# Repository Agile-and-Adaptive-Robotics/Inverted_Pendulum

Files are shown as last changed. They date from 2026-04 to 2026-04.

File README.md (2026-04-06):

# Inverted Pendulum

This repository contains the files related to the development, construction, and testing of the pneumatically-actuated Inverted Pendulum experimental rig, by members of the Agile & Adaptive Robotics Laboratory at Portland State University. The Inverted Pendulum was developed in tandem with the [Balance Platform](https://github.com/Agile-and-Adaptive-Robotics/Balance_Platform). The pair represents an experimental testbed for exploring perturbed bipedal stance, and was inspired by Peterka, 2002.

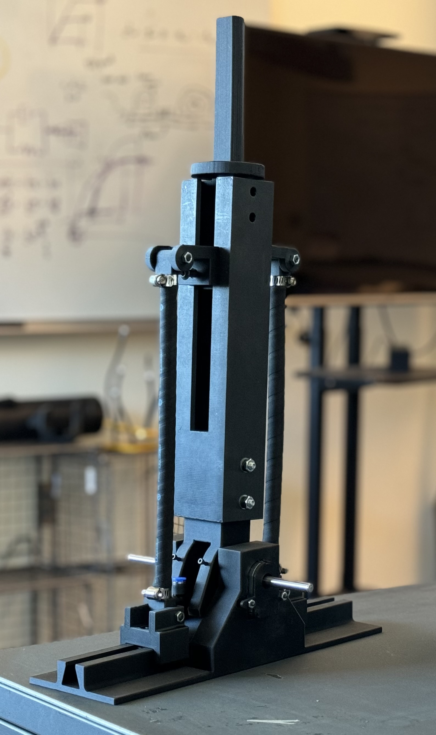
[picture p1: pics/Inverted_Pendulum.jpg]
Platform


Note that this repo is for the pitured version of the Inverted Pendulum. The previous repo was archived and can be accessed [here] (https://github.com/Agile-and-Adaptive-Robotics/Inverted_Pendulum-archive). 

## Contents

- [Software](/code)
  - [README](/code/README.md)
- [datasheets](/datasheets)
  - [README](/datasheets/README.md)
- [pics](/pics)
- [SolidWorks](/SolidWorks)

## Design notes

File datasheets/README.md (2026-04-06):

# Datasheets

This folder is intended to house data sheets for the hardware mounted to the Inverted Pendulum. Any related software should be copied to the proper folder and linked in this README file.

## Hardware 
*link to source, even if a hard copy is present*:

- [Festo_fluidic_muscle_DMSP](https://www.festo.com/us/en/p/fluidic-muscle-id_DMSP/)

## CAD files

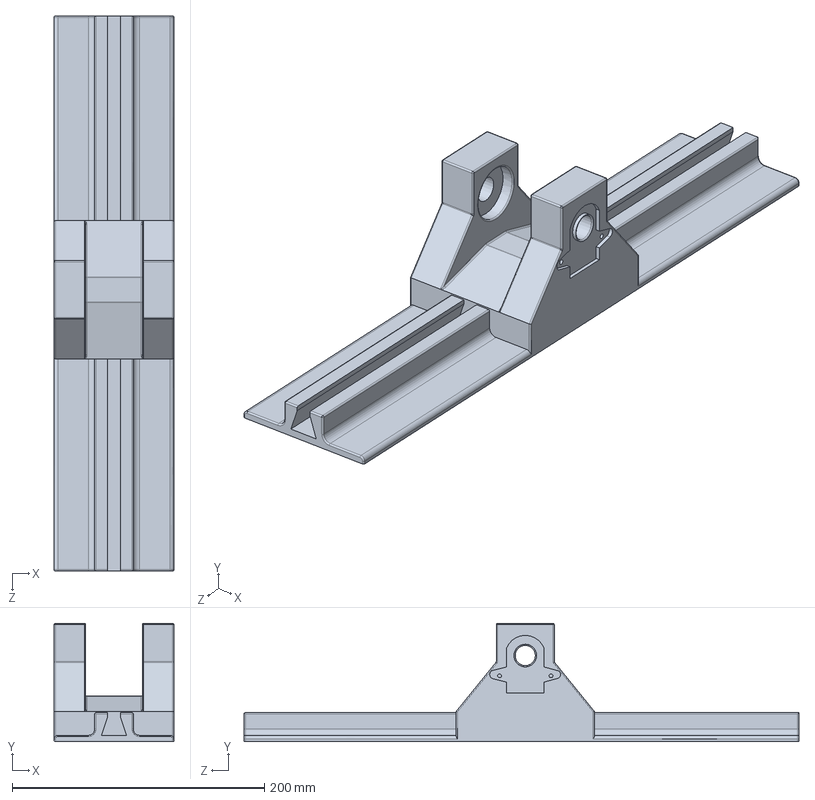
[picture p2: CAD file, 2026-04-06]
SolidWorks/IP_01_00_0000_Mechanical/AARL_IP_BottomPiece_001.SLDPRT
95.0 x 93.8 x 440.0 mm

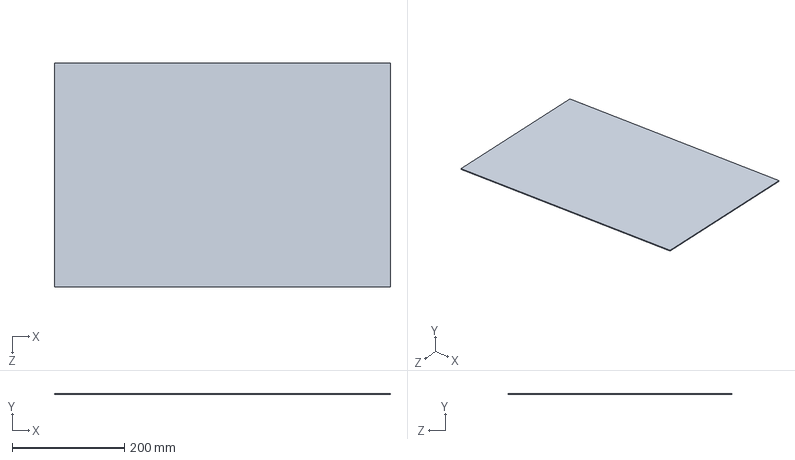
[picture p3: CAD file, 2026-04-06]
SolidWorks/IP_01_00_0000_Mechanical/AARL_IP_BasePlate_001.SLDPRT
600.0 x 2.00 x 400.0 mm

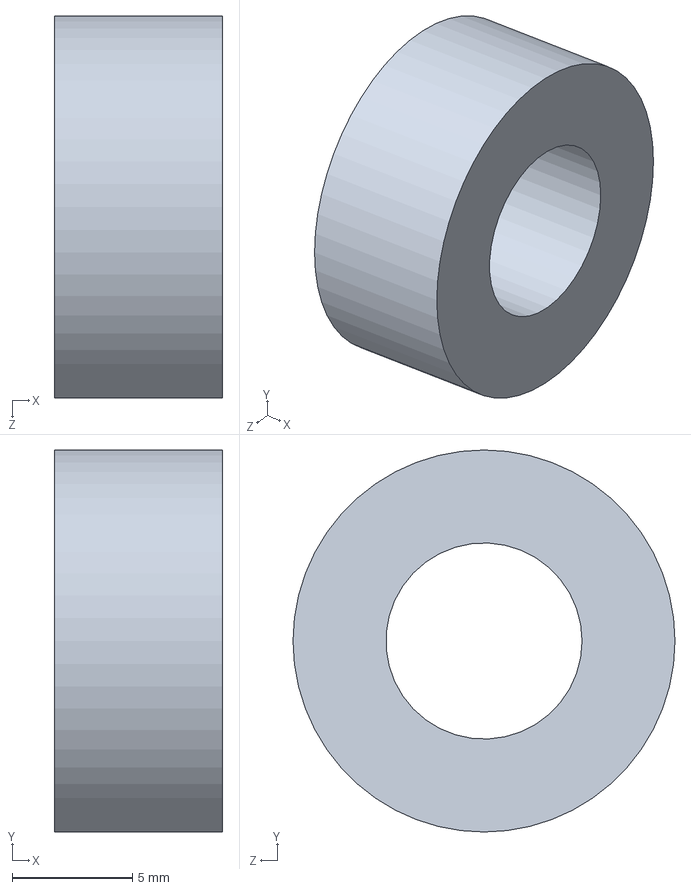
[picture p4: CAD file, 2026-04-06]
SolidWorks/IP_01_00_0000_Mechanical/AARL_IP_Joint_Rod_Insert_001.SLDPRT
7.00 x 15.9 x 15.9 mm

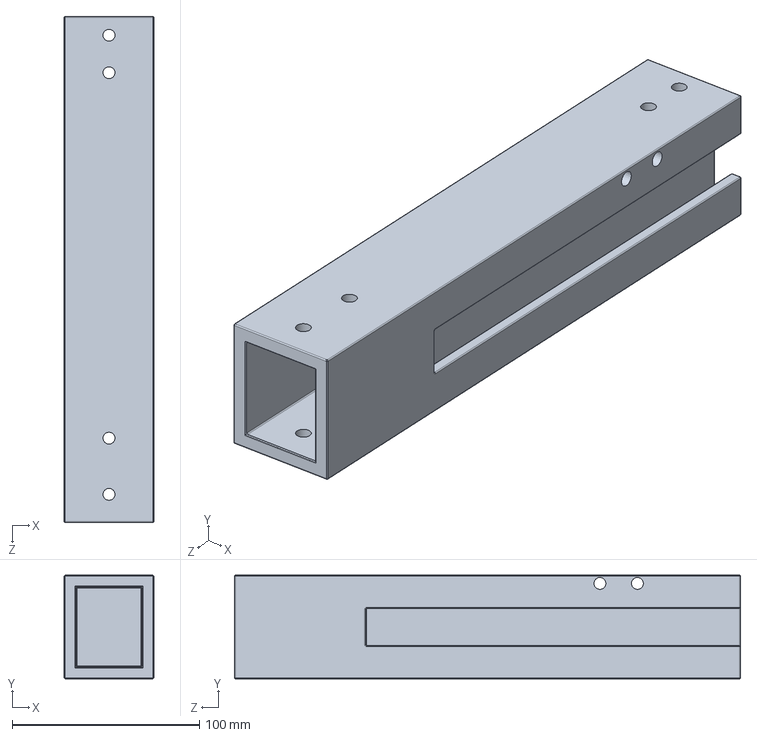
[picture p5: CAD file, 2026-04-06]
SolidWorks/IP_01_00_0000_Mechanical/AARL_IP_CenterPiece_001.SLDPRT
47.8 x 55.3 x 270.0 mm

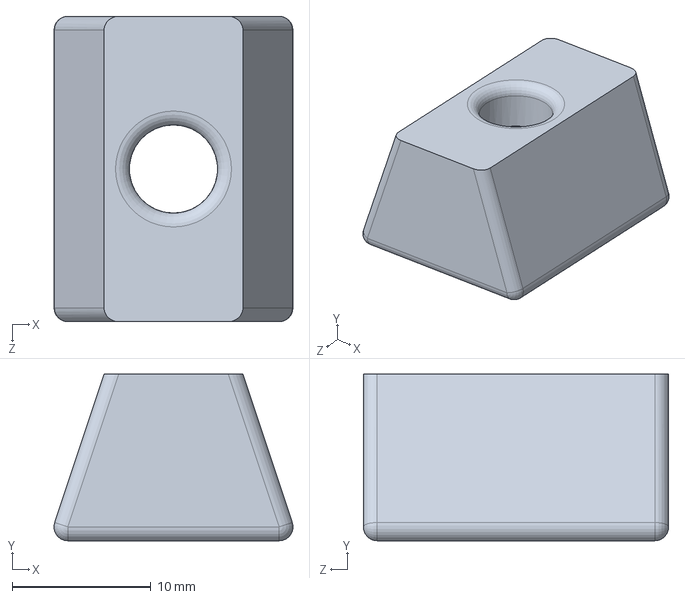
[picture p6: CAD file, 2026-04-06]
SolidWorks/IP_01_00_0000_Mechanical/AARL_IP_BottomSlider_BottomPiece_001.SLDPRT
17.2 x 12.0 x 22.0 mm

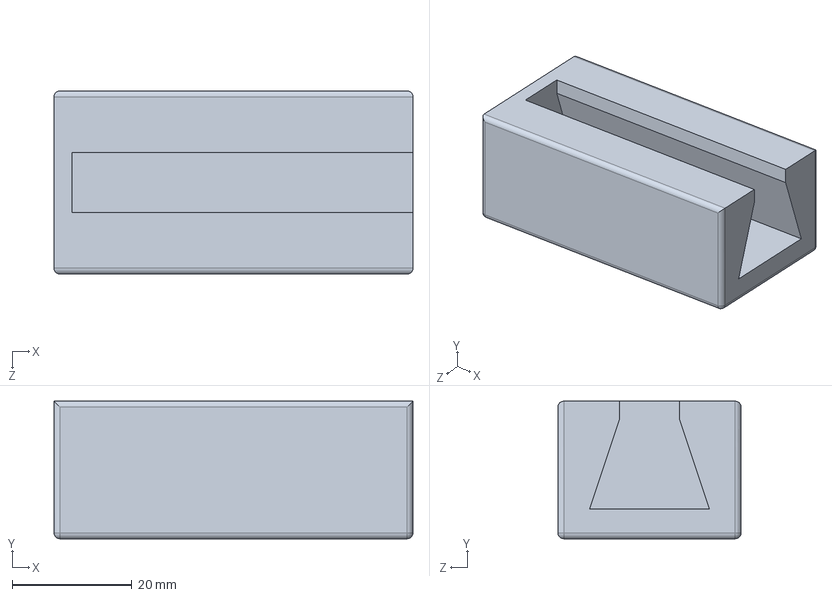
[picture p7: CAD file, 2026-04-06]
SolidWorks/IP_01_00_0000_Mechanical/AARL_IP_BottomPiece_Test_001.SLDPRT
60.0 x 23.0 x 30.7 mm

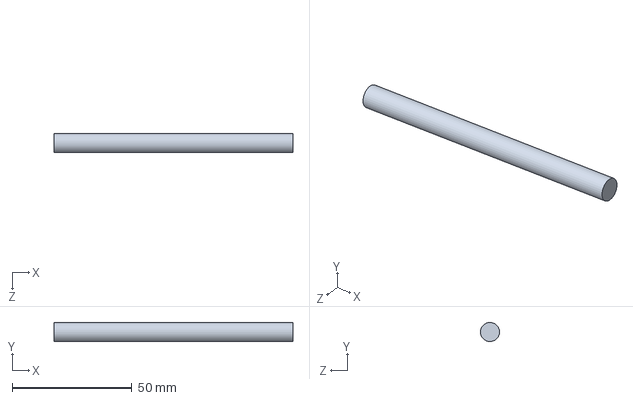
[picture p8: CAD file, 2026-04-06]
SolidWorks/IP_01_00_0000_Mechanical/AARL_IP_Joint_Rod_001.SLDPRT
100.0 x 7.99 x 8.00 mm

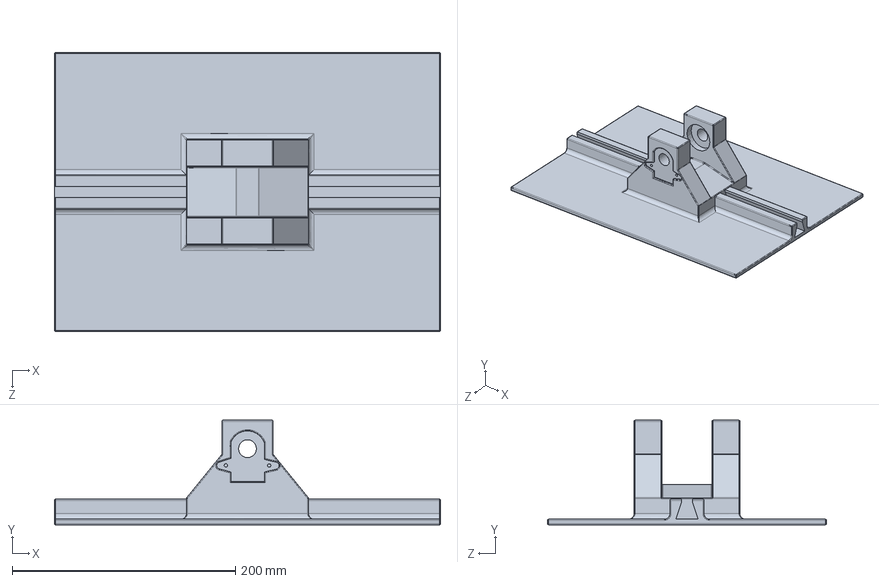
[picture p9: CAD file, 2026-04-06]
SolidWorks/IP_01_00_0000_Mechanical/AARL_IP_BottomPiece_002.SLDPRT
346.0 x 93.8 x 250.0 mm

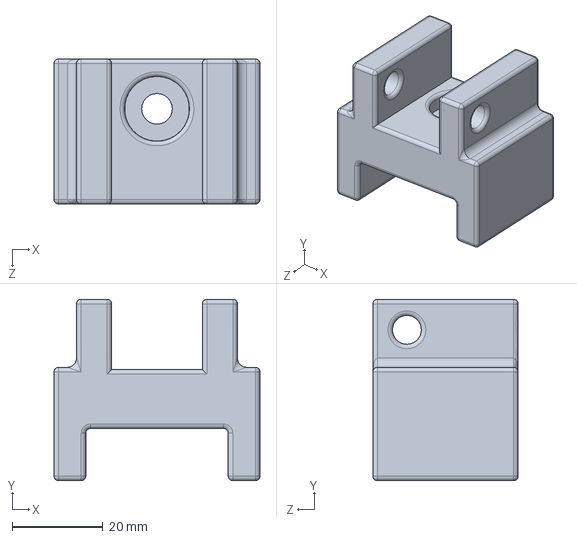
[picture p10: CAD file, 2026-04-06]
SolidWorks/IP_01_00_0000_Mechanical/AARL_IP_BottomSlider_TopPiece_001.SLDPRT
45.4 x 40.0 x 32.0 mm

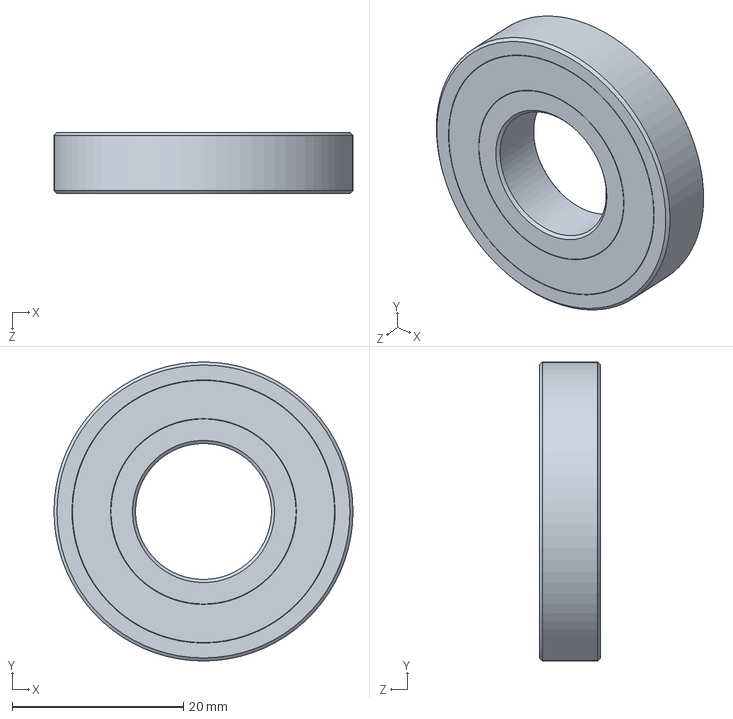
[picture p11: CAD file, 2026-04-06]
SolidWorks/IP_01_00_0000_Mechanical/AARL_IP_Joint_2342K167_PermanentlyLubricatedBallBearing_001.SLDPRT
34.9 x 34.9 x 7.14 mm

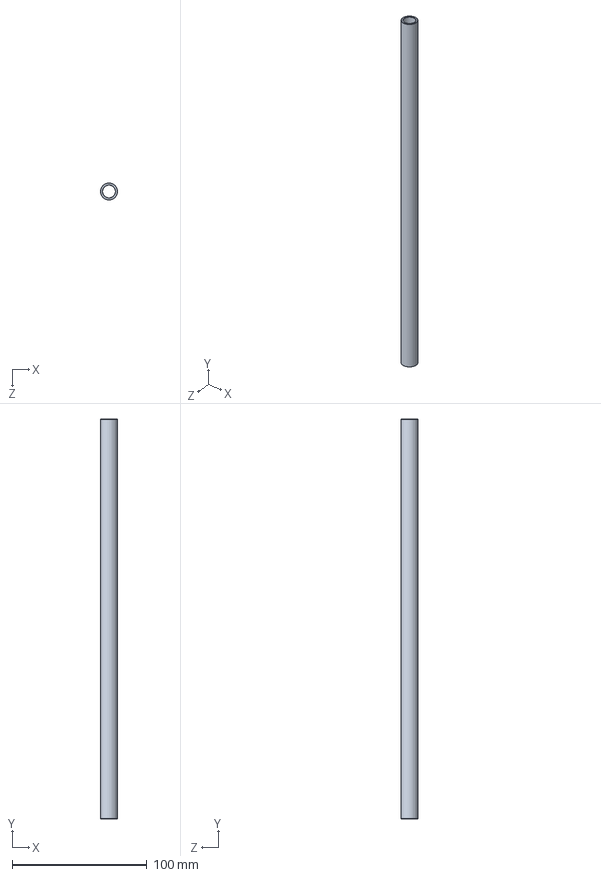
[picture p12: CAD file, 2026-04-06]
SolidWorks/IP_01_00_0000_Mechanical/AARL_QR_PN_PA_FL_WR_EX_001.SLDPRT
12.7 x 297.2 x 12.7 mm

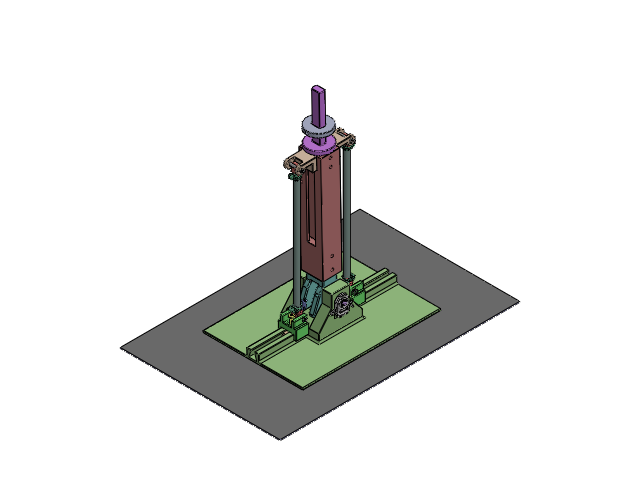
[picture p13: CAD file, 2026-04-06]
SolidWorks/IP_01_00_0000_Mechanical/Assem10.SLDASM
AARL_IP_BottomPiece_003
AARL_IP_BasePlate_001
AARL_IP_Joint_001
AARL_IP_Joint_2342K167_PermanentlyLubricatedBallBearing_001 x 2
AARL_IP_Joint_Rod_Insert_001 x 2
AARL_IP_Joint_Rod_001
AARL_IP_CenterPiece_001
AARL_IP_CenterSlider_001 x 2
AARl_IP_WeightHolder_001
AARL_IP_BottomSlider_BottomPiece_001 x 2
AARL_IP_BottomSlider_TopPiece_001 x 2
AARL_IP_90593A005_Black-OxideSteelHexNut_001 x 2
92981A105_Alloy Steel Shoulder Screws 30mm x 4
AARL_IP_BottomSlider_92137A545_AlloySteelFlangedButtonHeadScrews_25mm_001 x 2
AARL_QR_PN_PA_FL_WR_EX_001 x 2
AARL_Puppy_18_02_57_010-QSML-M3-4 x 2
AARL_Puppy_18_02_57_011-5388K140_Hose-Clamp x 4
AARL_QR_PN_EP_001 x 2
AARL_QR_PN_EP_001 edited x 2
90591A260_Zinc-Plated Steel Hex Nut (4) x 4
CUI_DEVICES_amt-102-top-cover-rev-h
CUI_DEVICES_amt-sleeve-rev-d(6 mm)
CUI_DEVICES_amt-hub-top-rev-d1
CUI_DEVICES_amt-hub-bottom-rev-b
CUI_DEVICES_amt10x-shaft-adaptor-rev-e
CUI_DEVICES_receiver-board
CUI_DEVICES_rotor-board-rev f
CUI_DEVICES_transmitter-board amt10(amt-102)
CUI1
91251A078_Black-Oxide Alloy Steel Socket Head Screw x 2
AARL_IP_WeightHolder_Top_001

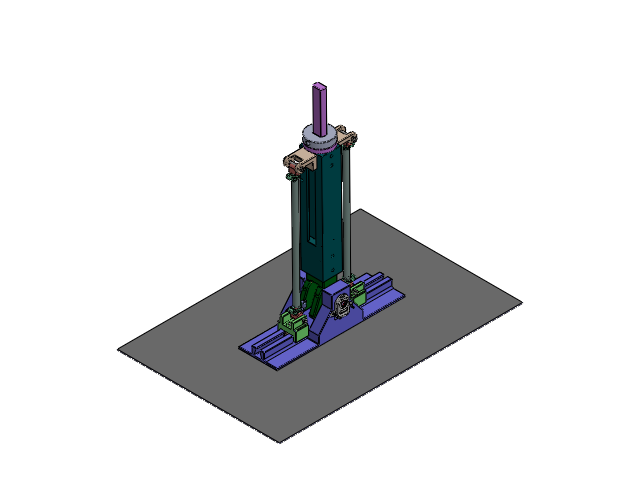
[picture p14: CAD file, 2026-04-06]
SolidWorks/IP_01_00_0000_Mechanical/AARL_IP_Assembly_001.SLDASM
AARL_IP_BottomPiece_003
AARL_IP_BasePlate_001
AARL_IP_Joint_001
AARL_IP_Joint_2342K167_PermanentlyLubricatedBallBearing_001 x 2
AARL_IP_Joint_Rod_Insert_001 x 2
AARL_IP_Joint_Rod_001
AARL_IP_CenterPiece_001
AARL_IP_CenterSlider_001 x 2
AARl_IP_WeightHolder_001
AARL_IP_BottomSlider_BottomPiece_001 x 2
AARL_IP_BottomSlider_TopPiece_001 x 2
92981A105_Alloy Steel Shoulder Screws 30mm x 4
AARL_QR_PN_EP_001 x 2
AARL_QR_PN_EP_001 edited x 2
90591A260_Zinc-Plated Steel Hex Nut (4) x 6
CUI_DEVICES_amt-102-top-cover-rev-h
CUI_DEVICES_amt-sleeve-rev-d(6 mm)
CUI_DEVICES_amt-hub-top-rev-d1
CUI_DEVICES_amt-hub-bottom-rev-b
CUI_DEVICES_amt10x-shaft-adaptor-rev-e
CUI_DEVICES_receiver-board
CUI_DEVICES_rotor-board-rev f
CUI_DEVICES_transmitter-board amt10(amt-102)
CUI1
91251A078_Black-Oxide Alloy Steel Socket Head Screw x 2
AARL_IP_WeightHolder_Top_001
91290A252_Alloy Steel Socket Head Screw 25mm x 2

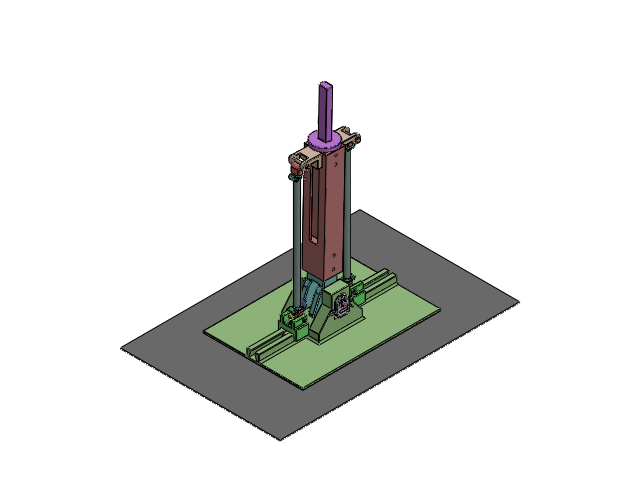
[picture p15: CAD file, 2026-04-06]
SolidWorks/IP_01_00_0000_Mechanical/AARL_IP_Ashir_002.SLDASM
AARL_IP_BottomPiece_003
AARL_IP_BasePlate_001
AARL_IP_Joint_001
AARL_IP_Joint_2342K167_PermanentlyLubricatedBallBearing_001 x 2
AARL_IP_Joint_Rod_Insert_001 x 2
AARL_IP_Joint_Rod_001
AARL_IP_CenterPiece_001
AARL_IP_CenterSlider_001 x 2
AARl_IP_WeightHolder_001
AARL_IP_BottomSlider_BottomPiece_001 x 2
AARL_IP_BottomSlider_TopPiece_001 x 2
AARL_IP_90593A005_Black-OxideSteelHexNut_001 x 2
92981A105_Alloy Steel Shoulder Screws 30mm x 4
AARL_IP_BottomSlider_92137A545_AlloySteelFlangedButtonHeadScrews_25mm_001 x 2
AARL_QR_PN_PA_FL_WR_EX_001 x 2
AARL_Puppy_18_02_57_010-QSML-M3-4 x 2
AARL_Puppy_18_02_57_011-5388K140_Hose-Clamp x 4
AARL_QR_PN_EP_001 x 2
AARL_QR_PN_EP_001 edited x 2
90591A260_Zinc-Plated Steel Hex Nut (4) x 4
CUI_DEVICES_amt-102-top-cover-rev-h
CUI_DEVICES_amt-sleeve-rev-d(6 mm)
CUI_DEVICES_amt-hub-top-rev-d1
CUI_DEVICES_amt-hub-bottom-rev-b
CUI_DEVICES_amt10x-shaft-adaptor-rev-e
CUI_DEVICES_receiver-board
CUI_DEVICES_rotor-board-rev f
CUI_DEVICES_transmitter-board amt10(amt-102)
CUI1
91251A078_Black-Oxide Alloy Steel Socket Head Screw x 2

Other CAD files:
SolidWorks/IP_01_00_0000_Mechanical/AARL_IP_Ashir.SLDASM
SolidWorks/IP_01_00_0000_Mechanical/Assem1.SLDASM
SolidWorks/IP_01_00_0000_Mechanical/AARL_QR_PN_PA_FL_WR_EX-Extensor.SLDASM
SolidWorks/IP_01_00_0000_Mechanical/AARL_IP_CUI_DEVICES_cui_devices_amt102-0048-i6000-w_001.SLDASM
SolidWorks/IP_01_00_0000_Mechanical/90591A260_Zinc-Plated Steel Hex Nut (4).SLDPRT
SolidWorks/IP_01_00_0000_Mechanical/91251A078_Black-Oxide Alloy Steel Socket Head Screw.SLDPRT
SolidWorks/IP_01_00_0000_Mechanical/91290A252_Alloy Steel Socket Head Screw 25mm.SLDPRT
SolidWorks/IP_01_00_0000_Mechanical/92981A104_Alloy Steel Shoulder Screws 25mm.SLDPRT
SolidWorks/IP_01_00_0000_Mechanical/92981A105_Alloy Steel Shoulder Screws 30mm.SLDPRT
SolidWorks/IP_01_00_0000_Mechanical/AARL_IP_90593A005_Black-OxideSteelHexNut_001.SLDPRT
SolidWorks/IP_01_00_0000_Mechanical/AARL_IP_BottomPiece_003.SLDPRT
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

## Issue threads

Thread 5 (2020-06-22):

### ISSUE TITLE
Conflicts after Branch Merged with Master

### ISSUE THREAD

**Issue by Reyna-5970** [Agile-and-Adaptive-Robotics/Inverted_Pendulum#5]
I'm not completely sure how it happened but after my last pull request (#4) was approved & merged, when I went to commit files to a new branch, there were conflicts in the files. I did fetch from origin (a couple times) before creating a new branch from master. When I reopened the files after merging, they seemingly returned to the state before I merged #4 with master, so I closed Solidworks and restarted the program. My files appeared as they should be (so that master was up-to-date with the latest version), but now I wonder if this resulted in file conflicts. I tried to commit anyway and might have created more problems in doing so...

**Comment by jakechung42** [comment]
I will look into this.

**Comment by jakechung42** [comment]
@Reyna-5970 this conflict occurs on tendonsAndSlots-ReynaAy-feat branch? When you created this branch, did you create this branch from master?

**Comment by Reyna-5970** [comment]
@jakechung42 I know that tendonsAndSlots-ReynaAy-feat as well as bpaMount-ReynaAy-feat were both created from master. If I just deleted bpaMount-ReynaAy-feat and then created a new branch from the most up-to-date master, should this resolve the issue?

**Comment by jakechung42** [comment]
You can try that, but you don't need to delete the old branches until you are sure that the issue is resolved.

**Comment by jakechung42** [comment]
However, the tendonsAndSlots-ReynaAy-feat branch is merged. It can be deleted.

**Comment by jakechung42** [comment]
I don't see the bpaMount-ReynaAy-feat branch. Have you published it?

**Comment by jakechung42** [comment]
I see the bpaMount-ReynaAy-feat now. The commit history of that branch is very wacky. It doesn't seem to have been created from the master branch. Can you make another branch of off master and copy to that branch your progress? (You might want to copy the files to a temporary location since when you switch branch, the content of that branch will also change)

**Comment by Reyna-5970** [comment]
I am trying to switch my current branch to master but it just shows the error message: `you need to resolve your current index first`

**Comment by jakechung42** [comment]
let's hope on Zoom. https://pdx.zoom.us/j/96739091812

**Comment by jakechung42** [comment]
Issue is resolved. The seems like the bpaMount-ReynaAy-feat branch was created when the master branch doesn't have all the updated features, so it created conflicts when Reyna tried to push.

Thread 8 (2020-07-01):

### ISSUE TITLE
IMU Wiring

### ISSUE THREAD

**Issue by Reyna-5970** [Agile-and-Adaptive-Robotics/Inverted_Pendulum#8]
At this point in the commit history for the electricalSchematic-ReynaAy-hdw branch (https://github.com/Agile-and-Adaptive-Robotics/Inverted_Pendulum/tree/4fdef6c5dde514bbfdee974c51bf0fd215c8dcdd), I have created a schematic on Eagle CAD of the possible electrical system we will use & mount onto the IP.

First off, I used an Arduino MEGA 2560, which I can change, but it's the one I have at home and offers ample opportunity for future improvement on the project.

Mainly, I wanted to double-check the IMU wiring. The datasheet can be found here: https://learn.adafruit.com/nxp-precision-9dof-breakout/downloads . Will the current configuration of the IMU wiring in the schematic work? If not, what should I change? I haven't worked with IMU's before.

I've also attached a screenshot of the most recent file in case there are any troubles with the commit history link. (The servos are for turning the tendon string spools... these may disappear depending on what we decide later on)

![image](https://user-images.githubusercontent.com/55515949/86060528-b9a88800-ba19-11ea-82b8-dc0cc20ddd25.png)

**Comment by Reyna-5970** [comment]
In addition, I would also like some advice on the valve manifold wiring. I need to change this still but was planning on hooking it up to digital pwm pins. Is this the correct signal type used?

**Comment by jakechung42** [comment]
This question should be addressed to @Scharzenberger. Cody, can you upload the datasheet of the valve manifold that we have also?

**Comment by jakechung42** [comment]
IMU has several communication protocols. It looks like you are using the SCL/SDA protocol.  The Mega has specific pins for SCL/SDA communication, which is pin 20 and 21. SDA on the IMU goes with SDA on the Mega, and same for SCL. I like your idea of controlling the tension string spool. Are those servos controlled using the PWM signal?

**Comment by jakechung42** [comment]
We also need to read data from the Encoder. to get the joint angle information. Let me find that data sheet.

**Comment by jakechung42** [comment]
Actually, you should have the datasheet for the encoder. It is in \Inverted_Pendulum\Documentation\Datasheets\Encoder_amt10.pdf

**Comment by Reyna-5970** [comment]
Yes, I'll work on adding in the encoder, just haven't gotten that far yet. The servos are using PWM. I always ignored the SDA and SCL labels since I didn't know what they meant but just now noticed them -- very cool! I will make that change.

**Comment by Reyna-5970** [comment]
![image](https://user-images.githubusercontent.com/55515949/86064646-80284a80-ba22-11ea-943b-061b08b12665.png)
(Updated version)

**Comment by jakechung42** [comment]
It looks good now.

**Comment by Scharzenberger** [comment]
**Datasheets**
I added the transistor array and valve manifold datasheets to the documentation folder.

Unfortunately, the valve manifold datasheet is mostly concerned with pneumatic diagrams -- so it won't actually be that useful.  In order to find the manifold pinout, we would probably have to look up the specific component that festo uses on their manifold.  I think I figured out the wiring from a hard copy datasheet that they sent with the manifold, if I remember correctly.

Fortunately, you can see the correct wiring for both the transistor array and the valve manifold on the transistor valve breakout PCB file I made for the quadruped.  It is this one: https://github.com/Agile-and-Adaptive-Robotics/Quadruped_Robot/blob/master/CAD_Electrical/Rev2/Valve_Breakout_Circuit/Transistor_Valve_Breakout_Circuit_Manual.brd

**Valve Manifold Advice**
The valve manifold requires 24 volts to switch on a valve.  You need to use a transistor array like this one [TransistorArray_TBD62783APG.pdf](https://github.com/Agile-and-Adaptive-Robotics/Inverted_Pendulum/files/4848477/TransistorArray_TBD62783APG.pdf), because the Arduino Mega cannot output enough voltage to switch the valves by itself.  You don't need to use that exact transistor array (since it has more channels than you need), but those will work and we should have some already (although, maybe getting low?).  The order is:

arduino --> transistor array --> valve manifold

**Can you use a PWM pin?**
You can use any digital pin(s) to connect to the transistor array, PWM or otherwise.  I am not an Arduino expert, since I usually just use the underlying microcontrollers.  If you were just using a stand alone microcontroller, you can use any digital pin for PWM applications...  So I don't understand why Arduino makes a distinction...

**IMU Advice**
I know that Connor was using I2C as the IMU communication protocol.  I haven't used those IMUs before, so I would ask Connor to show you his wiring diagram.

**Comment by Scharzenberger** [comment]
Also, a thought about the servos...  Depending on what servos you use, you may have problems with the servos being too weak to withstand the muscles.  If I am understanding correctly, the idea would be that you could use them to automatically pretension / tighten the muscle "tendons."  That is a good idea that will save a lot of time / effort down the line.  However, the servos would have to be decently strong to develop any sort of appreciable pretension in the tendons (which is still okay) and would have to be very strong to resist the force applied by the muscles (~100-150lbs).  Otherwise the spool would just unwind or the servo would break.

A possible fix to this would be to have a passive locking mechanism.  Once the servos reach there desired "tight" position, you would have a pin, screw, or other locking mechanism that engaged to passively maintain the muscle tension without the servos fighting the muscle.  This might be a bit of a struggle to implement, but who knows.

**Comment by Reyna-5970** [comment]
![image](https://user-images.githubusercontent.com/55515949/86159471-41949d80-babf-11ea-9889-6250e6bb132d.png)
I inserted the transistor array and just made an educated guess on the wiring. @Scharzenberger

**Comment by Scharzenberger** [comment]
Your educated guess is correct.  The transistor array looks good.  Good job!

When I check out the wiring I did for the valve manifold, I notice that there actually isn't a 24V supply pin.  There are 26 pins: 24  for the valves (which you have hooked up to the transistor array correctly), one for ground, and the final one is actually just a dummy pin.

I just added the pressure sensor datasheet to the inverted pendulum repository.  You could add those to your schematic (you need two, one for each muscle).  You only need the first three pins.  We have the MXP5700GP variant (there are many different variants in the datasheet, just look for that name, or the one with pins down and only a single spout).

Good luck!
[MPX5700.pdf](https://github.com/Agile-and-Adaptive-Robotics/Inverted_Pendulum/files/4853837/MPX5700.pdf)

**Comment by Reyna-5970** [comment]
![image](https://user-images.githubusercontent.com/55515949/86170243-ad7f0200-bacf-11ea-8abf-d23006f8639d.png)
For the wiring of the pressure sensors, is it more important that they go to analog pins or to serial? I found an example wiring diagram (below) and noticed that on the MEGA2560 A0 and RX0 are the same pin. In other words, should the second one be wired to A1 or RX1? Since it seems that the pressure sensor is likely analog then I assumed A1 was correct...
![image](https://user-images.githubusercontent.com/55515949/86170381-e61edb80-bacf-11ea-8eff-befdd654099b.png)

**Comment by Scharzenberger** [comment]
You are correct, the pressure sensors are analog.  It does not really matter which analog pins you use, but I would recommend not using the ones labeled RX or TX (e.g, you could use A2 & A3 instead).  I recommend this not because the RX and TX pins wouldn't work, but because they can also be used for UART serial communication (i.e., they are dual purpose).  Since there are free analog pins that are not dual purpose, we might as well save the RX / TX pins in case we decide to do serial port communication later.  Otherwise, looks good.

**Comment by Reyna-5970** [comment]
Awesome! Looks like the IMU is correctly wired according to this link: https://learn.adafruit.com/nxp-precision-9dof-breakout/pinout

Just wanted to document it here.

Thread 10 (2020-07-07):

### ISSUE TITLE
Eagle CAD Difficulties

### ISSUE THREAD

**Issue by Reyna-5970** [Agile-and-Adaptive-Robotics/Inverted_Pendulum#10]
I'm having some trouble with the Eagle CAD board layout for the custom arduino shield we're designing. When I update footprints and devices, it doesn't seem to transfer over the the PCB layout. Do you know why this would be?

Also I occasionally receive an error about a broken link between the schematic and board after closing the board file. I save the board and attempt to close it through the menu, but it still seems to happen. I suspect this might be the cause for the issue above, but am not sure how to address it.

**Comment by Scharzenberger** [comment]
Hey Reyna,

Sorry for being slow about getting back to you.  I am not 100% confident, but it sounds like your schematic and board files may have gotten out of sync.  This can happen if you only have one of them open while you edit the other (seems silly, but you need to have both open at the same time) or if you rename / change the path associated with either file.  Normally, whenever you edit something on the schematic (i.e., add a component, change the wiring, delete a component, etc.) these changes are automatically propagated to the board, but once you are out of sync, it starts having problems.

I was just googling about the out of sync issue and I don't see a ton that is very helpful.  It sounds like if they are out of sync, you have to go back and manually change the files to agree and then hopefully they will start updating together again.

You have probably already saw it, but there is a short discussion [here](https://www.element14.com/community/thread/43500/l/board-inconsistency-how-to-update?displayFullThread=true).

Sorry I don't have more advise.  I would just search up "eagle cad sync schematic and board" and see if you get anything helpful.

Let me know how it goes.

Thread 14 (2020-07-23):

### ISSUE TITLE
Double Checking Shield PCB Routing

### ISSUE THREAD

**Issue by Reyna-5970** [Agile-and-Adaptive-Robotics/Inverted_Pendulum#14]
![image](https://user-images.githubusercontent.com/55515949/87332163-0b5c1280-c4f0-11ea-8a18-19b11a445463.png)

I want to make sure that this will work -- and check-in to see if there are any changes you would make to the prototype. Once it's finalized, how does the ordering process work?

**Comment by jakechung42** [comment]
hmm, I have never done Arduino Shield PCB design before. Maybe @Scharzenberger might know something about this?

**Comment by Reyna-5970** [comment]
![image](https://user-images.githubusercontent.com/55515949/87335435-2aa96e80-c4f5-11ea-8808-d45b740329b5.png)

**Comment by Scharzenberger** [comment]
Hey Reyna,

I just looked over your PCB board.  Looks pretty good!  Here are a few notes / thoughts about what you have so far:

- @Conroy135 Can you confirm IMU wiring for us?  It looks like it could be right, but since you used them before, you will probably be able to tell immediately.

-If you aren't already doing this (looks like you are maybe?), you should make the bottom plane a ground plane.  I don't remember how off the top of my head, but you should make the bottom plane a ground plane (you should be able to figure out how by googling, since it is easy if I remember correctly).  This not only makes it very easy to connect things to ground, but also helps with noise, cooling, etc.  It is generally considered best practice to make one plane a ground plane in two layer boards and one plane a ground plane & one plane a power plane in four layer boards.

- Unfortunately, the valve manifold has a 26 pin connector, regardless as to how many pins you actually use...  So I would change the 4 pins you have representing the valve manifold to 26 pins (you have them labeled correctly, the extra ones would just be dummy pins).  This will let us easily plug the valve manifold in.

- Your transistor array looks correct in the schematic, but not on the board.  Not sure why this is, but check it out.  On the schematic, ground is on the same side as the valve manifold.  On the board, ground is on the other side for some reason?  Not sure what's going on there, but they should match.

- Just a thought for the encoder pins.  It would be very helpful to use screw terminals.  Something like this: [https://www.amazon.com/DIYhz-green-Terminal-Connector-Arduino/dp/B07B79Q911/ref=zg_bs_306731011_50?_encoding=UTF8&psc=1&refRID=3M66JXG2FXZTV3SJHGGR](https://www.amazon.com/DIYhz-green-Terminal-Connector-Arduino/dp/B07B79Q911/ref=zg_bs_306731011_50?_encoding=UTF8&psc=1&refRID=3M66JXG2FXZTV3SJHGGR).  That way we don't have to solder the encoder wires to the breadboard (and not have to unsolder them to replace them / fix issues).

- Where is your +24V connection?  We are going to need to plug it into the shield somewhere.  I would again suggest using a screw terminal (like above).  Have a +24V & GND pair.  Then take the +24V over to the transistor array.  It looks like the transistor array might currently be attached to +5V, which is not correct (despite the fact that it looks right on the schematic...?).  The +24V line will also need a bigger than usual trace.  You can look up what the rule is, but I think it is like 1mil per volt or something.  So it would be about 20mils wide?  (Double check, but I think that is about right).

Not a big deal, but here are some routing best practices to keep in mind (you have a relatively big board with relatively few components, so it is not as critical, but still a good idea):

- Use the smallest angle bends possible.  e.g., avoid 90 deg bends (use two 45 deg bends instead).

- Minimize non-ground lines on the bottom plane.  Put as many lines as possible in the top plane.

- Use as short of traces as possible.

- Minimize the use of vias.  Yes, this is in direct contradiction to the "use as short of traces as possible" goal.  You have to balance the two. I will generally prefer to use vias if it means that I can make the wiring shorter and more organized.

- Make the traces in each area go more or less in the same direction.  If you have to via to the bottom plane, try to pick a consistence direction to move in the bottom plane (e.g., up-down or left-right).

Overall, looks pretty good.  If you can figure out what is wrong with the transistor array, then the other stuff is more just quality of life improvements (not fatal).

Let me know if you have any questions.

Best Regards,

Cody

**Comment by Conroy135** [comment]
IMU connections look good! I haven't used a mega with an IMU so there might be some issues, but that will likely come from code complications.

**Comment by Scharzenberger** [comment]
Hey Connor,

Thanks for the feedback.  Do you remember the name of the library you were using to communication with the IMUs?

**Comment by Conroy135** [comment]
I used the various libraries from Adafruit. If you have a specific IMU, Adafruit likely has a good library to use for it. It will also need the wire.h library, which can be found in the Arduino IDE without any outside installation.

**Comment by Reyna-5970** [comment]
@Scharzenberger What's does the footprint of the valve manifold pins look like? Is it 2x13, 1x26... etc.? Also, it might just be easier to put the valve manifold off of the platform all together and just plug in the pins needed, because I imagine having the manifold directly mounted would dramatically alter the balance of the platform.

**Comment by Scharzenberger** [comment]
Hey Reyna,

The footprint for the valve manifold connector is 2x13 (standard pitch, whatever that is. :p).  I agree -- the valve manifold is pretty heavy, so that could screw things up.  Regardless as to whether the valve manifold is mounted to the platform, the easiest way to electrically connect it will still be to use the 2x13 connector.  The connectors it has lock it into place so it doesn't come unplugged.  If we just used wires, we would either have to solder to the manifold (which I wouldn't do, because the manifold is expensive and we would have to unsolder to remove it) or use the female jumper cables (which get unplugged very easily).

**Comment by Reyna-5970** [comment]
![image](https://user-images.githubusercontent.com/55515949/87467343-a9250f80-c5cc-11ea-91b8-0d93bf330383.png)

I made the suggested improvements and tried to make the routing as short as I could. As far as the IMU, since that's being mounted onto the tibia, should I change the footprint? The pins shouldn't need to be as spaced out, right?

**Comment by Scharzenberger** [comment]
Hey Reyna,

Looks better.  You are right about the IMU, it will be mounted to the tibia.  Only wires will come back to the board, so you could use more screw terminals for that.

Is this a conflict?  It kind of looks like the wires are crossing...

![Inked87467343-a9250f80-c5cc-11ea-91b8-0d93bf330383_LI](https://user-images.githubusercontent.com/57116010/87473441-50f30b00-c5d6-11ea-80b6-dfe5d1583b1e.jpg)

Also, this looks like maybe a conflict?  Not sure...

![Inked87467343-a9250f80-c5cc-11ea-91b8-0d93bf330383_LI](https://user-images.githubusercontent.com/57116010/87473675-ae875780-c5d6-11ea-824c-2a15fa663877.jpg)

**Comment by Reyna-5970** [comment]
Whoops, I'll fix those things! I was dragging around the wires a bit so that's why that happened. I'll also change the IMU wiring to screw terminals.

**Comment by Reyna-5970** [comment]
![image](https://user-images.githubusercontent.com/55515949/87488515-75121480-c5f5-11ea-8d09-638d632dde04.png)
Changed the IMU input to screw terminal and fixed intersecting wires. If I dimension the PCB as such then will the holes that are going off of the board be an issue in manufacturing? This is more of an Eagle CAD specific question @Scharzenberger

**Comment by Reyna-5970** [comment]
Also, noticed that the wrong pin was square on the pressure sensor footprints so I changed that.

**Comment by Reyna-5970** [comment]
![image](https://user-images.githubusercontent.com/55515949/87593700-b7446000-c6a0-11ea-836a-114f2616bb1b.png)
Some of the text looks like it's overlapping but it shouldn't be. I added the text I want printed to the silkscreen layer "tPlane" and I believe the other text is just placed from before (when the devices were created for the schematic). I fixed the encoder wiring to go to interruptible pins: 2, 3, 18. I also added a ground plane.

**Comment by jakechung42** [comment]
Do you have a schematic view of the wiring similarly to this for the new design?
![image](https://user-images.githubusercontent.com/33278786/87600991-16a66e00-c6a9-11ea-9cf2-7560b1db2d07.png)
It's quite hard looking at the PCB wiring with all the labels like this. Thank you.

**Comment by Reyna-5970** [comment]
![image](https://user-images.githubusercontent.com/55515949/87601218-7f8de600-c6a9-11ea-9186-8bf28233c14e.png)

**Comment by jakechung42** [comment]
The wiring looks good. I don't know if Cody wants to add anything else.

**Comment by Scharzenberger** [comment]
Hey Reyna, it looks pretty good.  Glad you got the ground plane to work!  I think the wiring looks correct.

You have probably already tried messing with it, but you should be able to go in and move around, rotate, scale, etc all of the silk screen text.  Making some of it a bit smaller would probably help fitting it all on the board (since right now a lot of it is over lapping).  You only really need to label spots where there are connections to the board (like the screw terminals.  You don't really need to label the pins that are only internal to the board, because presumably, that will all be set up correctly and the user (e.g., you or us) won't have to worry about that at assembly time.  I would definitely leave the device names though.  If you can find the part number for the transistor array, it would probably be good to include that.  Same thing for the part number of the pressure sensors.

Now that it is mostly together, you can go to Osh park's website and see how much it will cost to make (but don't buy it yet -- you will need the lab's account info anyway): [https://oshpark.com/](https://oshpark.com/).  Their website walks you through it if I remember correctly.  Also, it will show you what the board will look like and tell you if it thinks there are problems with your file.

Good luck!  Let me know if you have any problems.

**Comment by Reyna-5970** [comment]
![image](https://user-images.githubusercontent.com/55515949/87974135-6eb0ec00-ca7e-11ea-8c11-3b8a86da91a0.png)
Is this okay? @Scharzenberger

**Comment by Reyna-5970** [comment]
![image](https://user-images.githubusercontent.com/55515949/88230427-44e6f900-cc27-11ea-8a5b-82136694f586.png)
I increased the width of the 24V wire. Plus, I added on a spot for this [MicroSD Adapter](https://www.adafruit.com/product/254) to plug-in to the shield.

I still need to look into how to remove the extra holes, but otherwise this is just an update about what I've done so far.

**Comment by Reyna-5970** [comment]
Also, the resistor connected to Pin 9 is supposed to be a pull-up resistor for the CD pin.

**Comment by Reyna-5970** [comment]
Another update: found [this link](https://learn.sparkfun.com/tutorials/pull-up-resistors) explaining more about pull-up resistors so I fixed the wiring on that. Looks like we don't necessarily need to use the CD pin because it's just to detect whether there's a SD card actually plugged in or not, but just in case, I thought I'd include the wiring to be ready.

**Comment by Reyna-5970** [comment]
![image](https://user-images.githubusercontent.com/55515949/88241433-f04f7800-cc3e-11ea-8f3c-a803d83141b2.png)

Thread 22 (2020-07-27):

### ISSUE TITLE
Recent pull-request restored old version of CAD files

### ISSUE THREAD

**Issue by Reyna-5970** [Agile-and-Adaptive-Robotics/Inverted_Pendulum#22]
Molly was working on the main assembly but within a branch that was not fully updated at the time (I believe due to github errors with committing to a branch that had already been merged). The branch in question is from pull request #20.

However, in the branch minorFootAdjustments-ReynaAy-feat from pull request #17, I had made quite a few small edits to the foot assembly, which now appear to be overwritten by the most recent branch merging. Is there a way to recover this version of just the foot assembly (at the time, I did not edit the overall assembly nor the tibia assembly)?

**Comment by jakechung42** [comment]
I haven't deleted the branch minorFootAdjustments-ReynaAy-feat, so you should be able to get that file in that branch.

- In GitHub Desktop, navigate to that branch and copy the foot assembly file that you want.
- Store it in a temporary location outside of the GitHub directory.
- Switch to the branch that you are working on where you would want to foot assembly file.
- Bring the foot assembly file from the temporary location and paste it in the GitHub directory. 

Try that, I think that shouldn't cause any conflict.

**Comment by Reyna-5970** [comment]
Seemed to work, thanks!
